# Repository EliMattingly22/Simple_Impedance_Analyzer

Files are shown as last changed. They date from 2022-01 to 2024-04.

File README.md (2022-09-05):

# Simple Impedance Analyzer

## Purpose

The impedance analyzer was designed as a low-cost, flexible, and accurate platform to perform impedance measurement at arbitrary frequencies up to ~250kHz. The current infrastructure assumes the user has access to a National Instruments DAQ (e.g. NI-USB-6363), though similar digitizers would be similarly effective. 

In this current configuration:
* About 0.1% Accuracy for large impedance and frequency ranges.
* The LabView has an easy to use GUI
* TDMS file saving
* It can measure impedances from 10mOhms to 10MOhms, and by changing the shunt resistor values that range could be extended 
* Test at frequencies from DC-250kHz (>100kHz still needs validation)
* Perform frequency sweeps on log or linear spacing
* If a battery-powered computer and DAQ is used, the entire measurement apparatus can be both portable and floating.



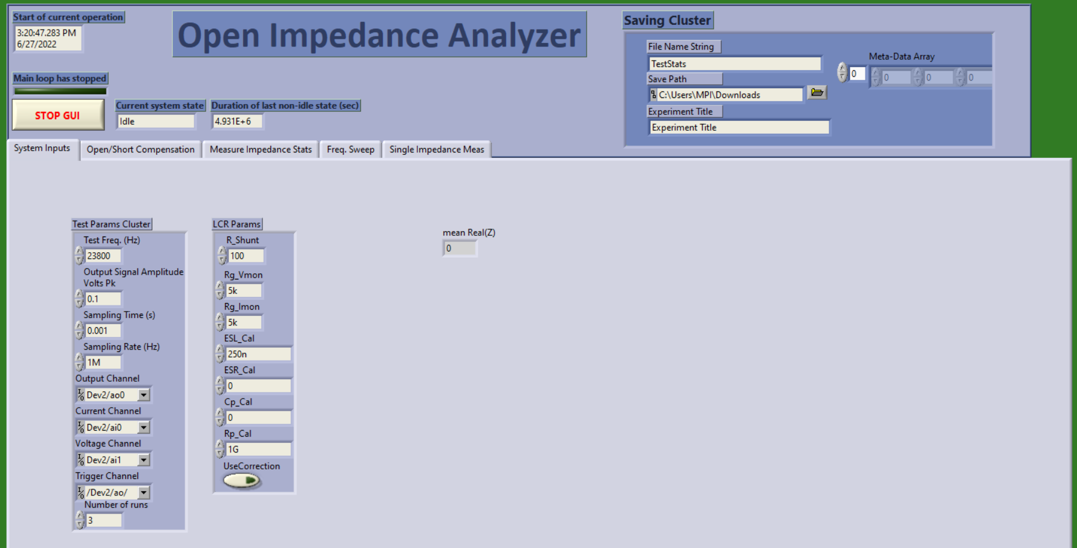
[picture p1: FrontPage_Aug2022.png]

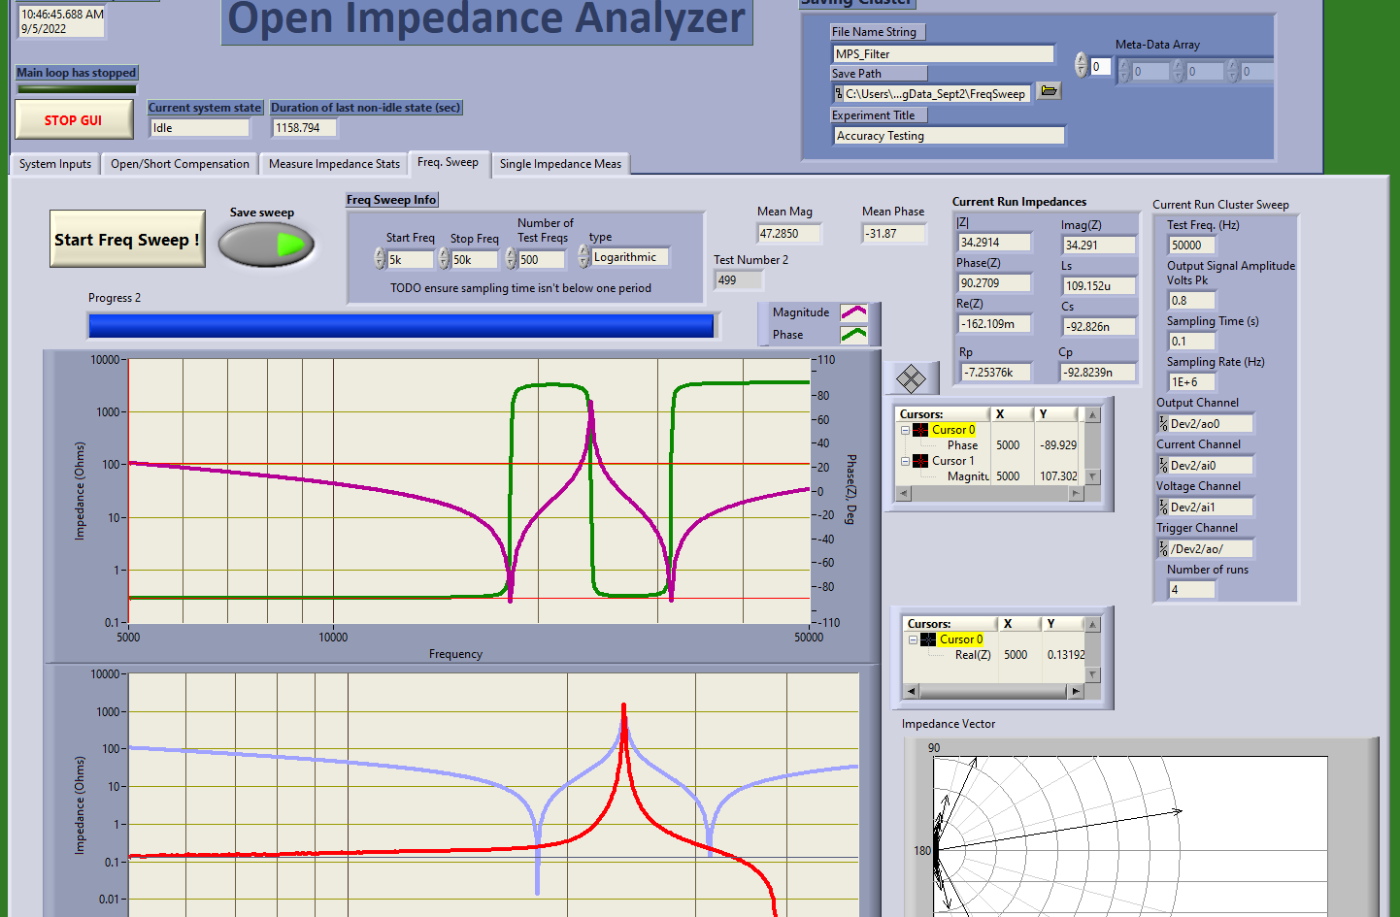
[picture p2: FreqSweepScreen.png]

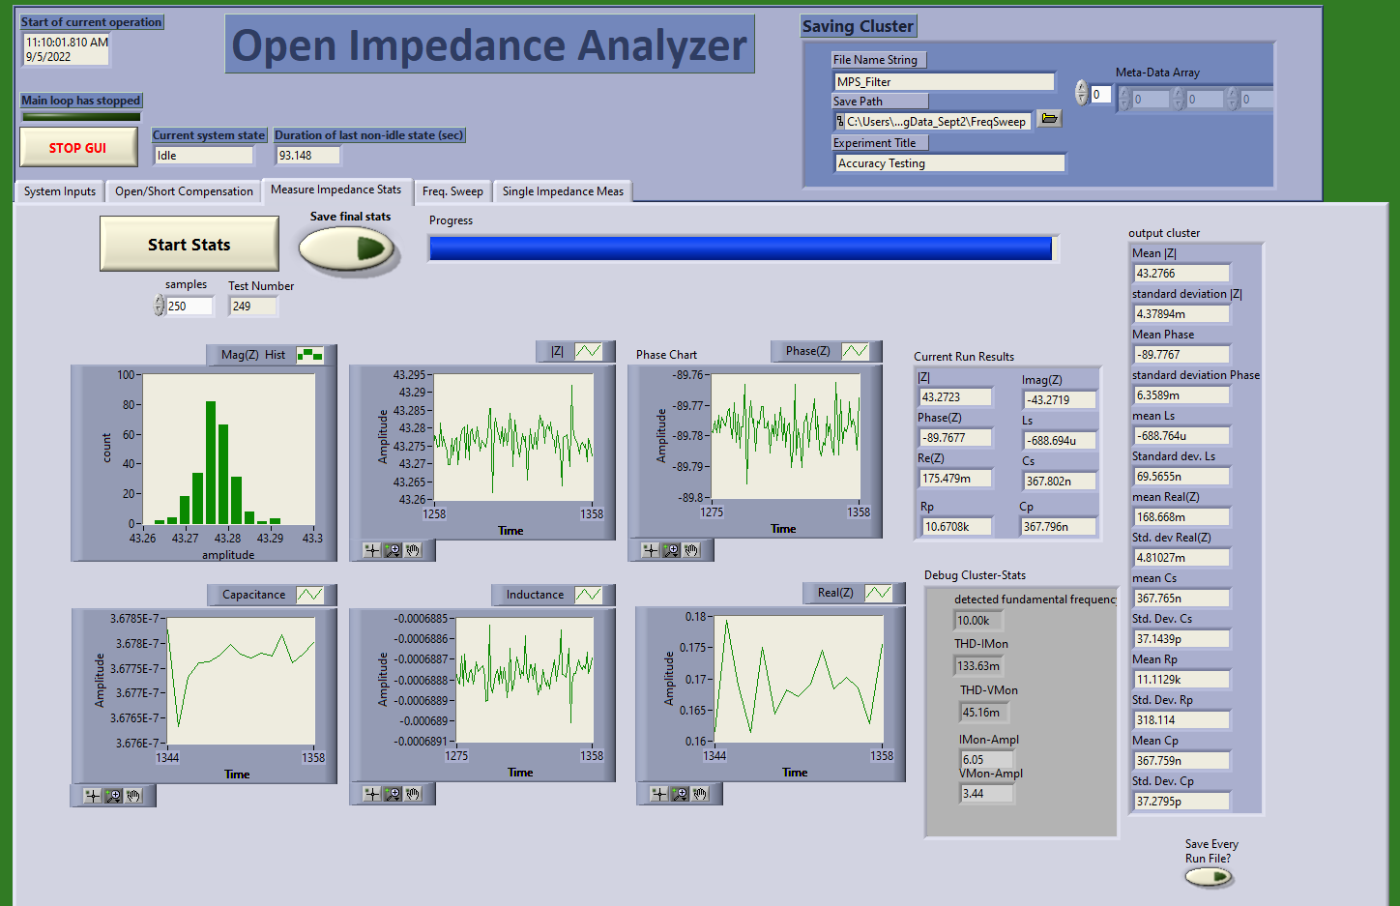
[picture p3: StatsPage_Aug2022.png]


### Accuracy and noise (1 kHz resistive)
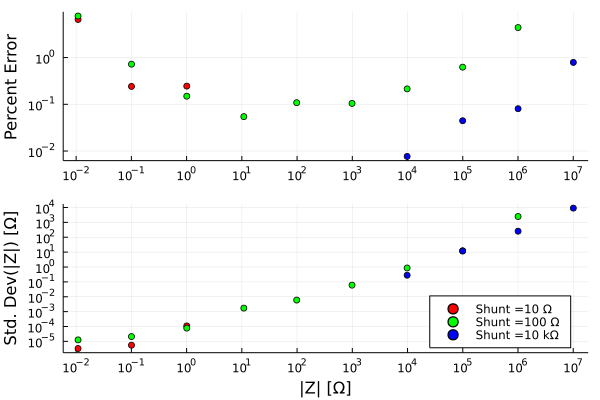
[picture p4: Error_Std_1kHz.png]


### Accuracy and noise (10 kHz resistive)
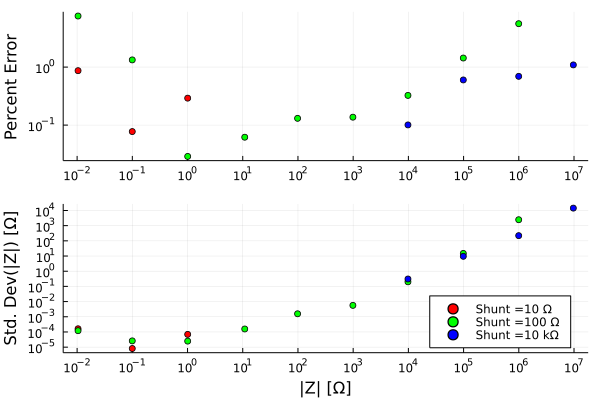
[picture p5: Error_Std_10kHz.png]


### Accuracy and noise (100 kHz resistive)
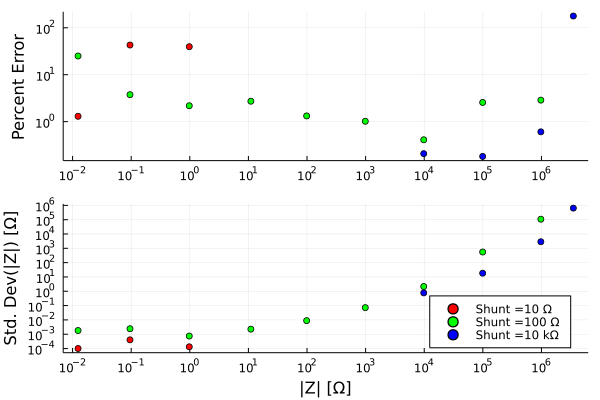
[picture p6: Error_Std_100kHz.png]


### Accuracy and noise (10 kHz Capacitors)
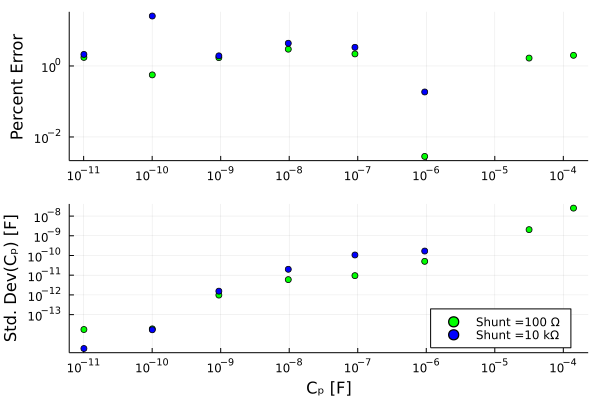
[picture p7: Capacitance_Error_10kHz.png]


* It seems one can expect about 1% accuracy between 10 p to 0.1 mF. 
* The point indicating 0.01% accuracy is probably spurious. Some random errors happened to offset each others. 

# PCB
Use V2 rev B. V3 has not been tested/built. it is still in design phase. Perhaps it should just be in a separate brach of Github. Designed in KiCAD v6.

# Operating Principle
This circuit uses the "auto-balancing bridge" technique. If you are curious/want to play around with the circuit you can see the LTSPICE schematic. 

It is worth reading the [Keysight impedance measurement handbook](https://www.keysight.com/us/en/assets/7018-06840/application-notes/5950-3000.pdf) or TI's reference design for an LCR meter front-end for an overview of measurement techniques. 

The current through the DUT is (ideally) the same as the current in the shunt resistor, so the impedance is V(DUT) / (V(Shunt)/R(Shunt)). 

# Source of Errors

The precision of the circuit is dominated by the shunt resistors and gain accuracy of the INAs. Error in any of these will linearly cause an error in the calculated impedance. If they are stable over time, they can conceivably be calibrated with a high tolerance (e.g. 0.01%) reference resistor.

If the shunt resistor is off by some value, *X* (where 1.01 would be 1% higher than nominal), the current would be reported as I<sub>0</sub>**X* where I<sub>0</sub> is the actual current. 

The noise performance of the INAs isn't great, but the FET inputs have extremely low bias currents, and low current noise, which are necessary if high impedance loads are attached. The noise should add an incoherent error, so by averaging for longer, this can be mitigated. 

The parasitic elements can be accounted for by taking an open/short/load measurement. See sect. 4.3.2 in the impedance measurement handbook

# Operation instructions
## Setup
The device should be plugged in with a four-wire (Kelvin) probe attached. On the probe there will be two pairs of leads, each connected to a clamp (typically one pair is red, one is black). The two BNC connections on the red lead should be plugged into the "HPot" and "HCur" connectors, and the BNCs on the black probe should be connected to "LPot" and "HPot" connectors. 

Plug in the power and make sure the LEDs next to the "+5V" and "-5V" are illuminated. 

The DAQ should be plugged in via the BNC connectors and however they are connected, those outputs/inputs are selected on the front page of the Labview GUI.

Also on the front page, set the sampling rate to the maximum allowable (see documentation for your DAQ). Set the sampling time to be >10 periods of whatever frequency you are testing at. Longer gives better noise performance.

For the shunt resistor, use the value most similar to the load you are measuring. Use J13/14 to select the shunt resistor. 

Set the series resistor before the load (R9/24) to the same value as the shunt resistor using J17.
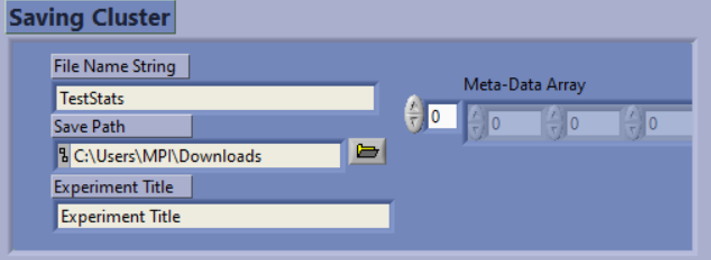
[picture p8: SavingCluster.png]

* For the saving cluster the Fine Name String will be the identifier in the file name.
* Save path is the directory it will be saved within
* Experiment title is a string added to the metadata
* Meta-data array is an array that the user can fill in as desired. It just goes into meta-data as-is. For example, if you are measuring the turns on an inductor vs inductance, you could enter the turn count in this spot and then afterwards when processing the data it would already be saved. 

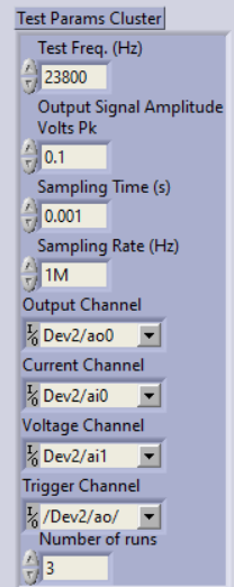
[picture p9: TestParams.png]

* **Test Freq:** This is the measurement frequency for single measurements and stats. It is overwritten for frequency sweeps.
* **Output Signal Amp:** This is the waveform amplitude the DAQ outputs. If this is too low, SNR is sacrificed, if it is too high, the waveform can clip. Check the debugging cluster to ensure the amplitude of the voltage monitor and current monitor arent clipping (i.e. they are less than 7 V or so)
* **Sampling time:** Time of acquisition in seconds. Should be long enough for 10 or so periods of the output waveform. More improves SNR. 
* **Sampling Rate:** Sampling rate in Hz. should be maximum allowable.
* **Output Channel:** The channel that goes into the Voltage Input BNC (top left in photo above)
* **Current Channel:** The channel that comes from the current sense BNC (Bottom left in photo above)
* **Voltage channel:** The channel that comes from the voltage sense BNC (middle left in photo above)
* **Trigger channel:** This should be set to the output start trigger, for example "/Dev2/ao/StartTrigger"
* **Number of runs:** this is the number of times the acquisition will be repeated and averaged.

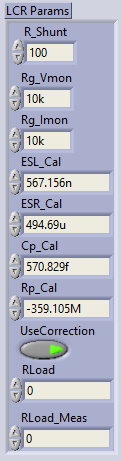
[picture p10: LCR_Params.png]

* **R_Shunt:** The shunt resistor value (R14/18)
* **Rg_Vmon:** The gain-setting resistor for the voltage monitor (R12 or R8) 
* **Rg_Imon:** The gain-setting resistor for the current monitor (R11 or R7) 
* **ESL_Cal:** This value is set by the short circuit compensation and is enabled by the UseCorrection boolean
* **ESR_Cal:** This value is set by the short circuit compensation and is enabled by the UseCorrection boolean
* **Cp_Cal:** This value is set by the open circuit compensation and is enabled by the UseCorrection boolean
* **Rp_Cal:** This value is set by the open circuit compensation and is enabled by the UseCorrection boolean

* **UseCorrection:** enables the short/open compensation values. Typically set to TRUE (green illuminated)

* **RLoad:** This is the actual value of the load compensation resistor that one may use to calibrate gain errors of the system. 

* **RLoad_Meas:** This is the measured value of that load. To acquire this value, set RLoad and RLoad_Meas to 0 and then measure the known load and set this and the RLoad by typing in the appropriate values.

## Calibration
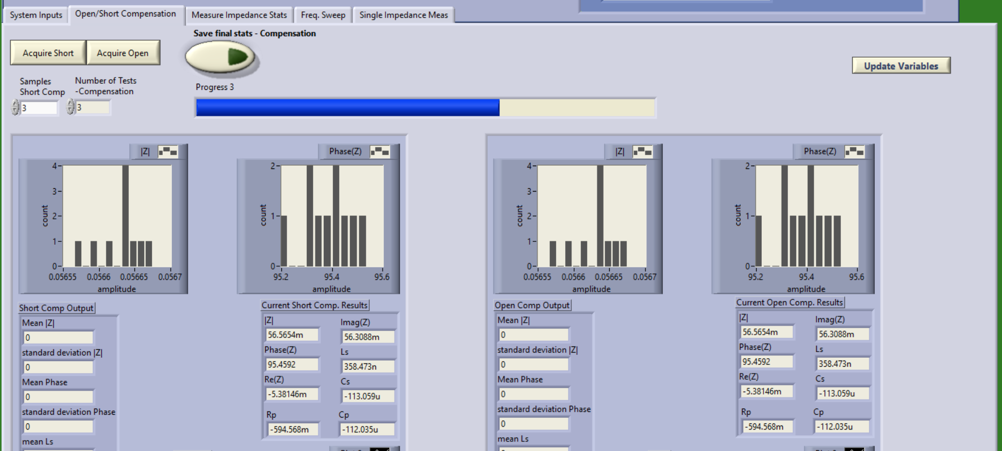
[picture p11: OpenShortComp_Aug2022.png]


Set the equipment up to measure your load, and short the clips together. Next, go to the Short/Open compensation tab and press the "Acquire short" button. Open the clips and then do the open compensation.

## Measure load

Use the last page to do a single impedance measurement and ensure the load is similar to expected. Then use the stats page or freq sweep depending on what you want. 

## List of jumpers & their purpose
* J15/16 low-pass filters for the input. These clean the analog signal from the DAQ. They can generally be set to the highest frequency that the user plans to measure. Removing the jumper disconnects the filtering entirely.

* J10: The current monitor gain selection
* J12: Voltage monitor gain selection
* J13/14: Shunt resistor selection
* J17: Series resistor selection. This resistor in series with the load helps stability and makes the system more balanced. The resistor value should match the shunt resistor value.

# If you are having errors:
1) Make sure the channels are selected properly
2) Make sure BOTH sides of the clips are on the load
3) Make sure the BNCs are properly attached
4) The LEDs should be illuminated
5) The amplitude should be sufficiently low that it doesn't saturate the inputs/clip

# Example applications:

## Litz wire, air-core inductor
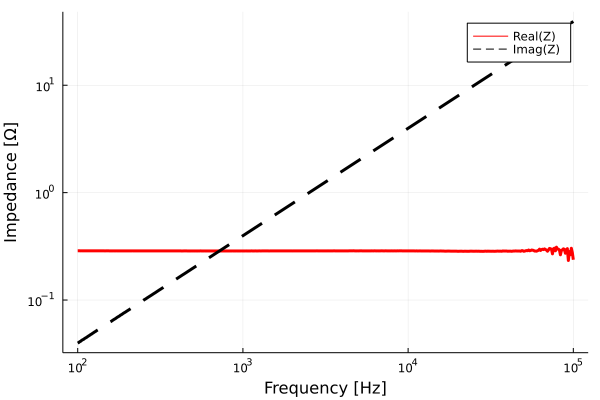
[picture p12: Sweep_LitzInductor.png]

* The impedance is exactly as expected here for an inductor. Because Litz wire was used, the resistance is not a strong function of frequency. 
* The slope of the reactance is constant and proportional to frequency.

## Skin and proximity effect on inductor
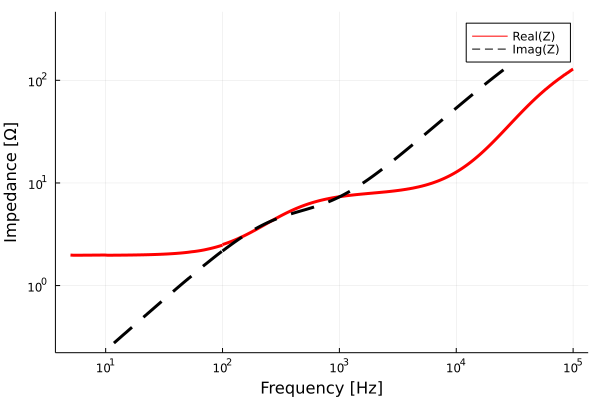
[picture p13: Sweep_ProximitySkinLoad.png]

This is a frequency sweep of a solenoid (~1 mm diameter) wound on a copper tube with a wall-thickness of ~1 mm. Quite a lot is happening with this load:
* Below 50 Hz or so, it is essentially a resistor, the inductive impedance is very small. 
* At 50-1k Hz, the solenoid's impedance has an increasing real component and decreasing inductance (decreasing slope of imag.). This occurs as the inductor couples more strongly into the copper tube. The inductance decreases because the magnetic field in the center of the tube is decreasing as the wall effectively shields it. 
* Between 1k and 10k Hz the resistance nearly plateaus and the inductance starts rising proportionally to frequency. Presumably at this point, the skin depth of the copper tube has been met, so the magnetic fields are not significantly penetrating to the center of the tube. 
* Above 10 kHz the skin depth of the wire is being reached and the AC-resistance is increasing as the effective copper area for current to flow in decreases.

## Resonant L-C
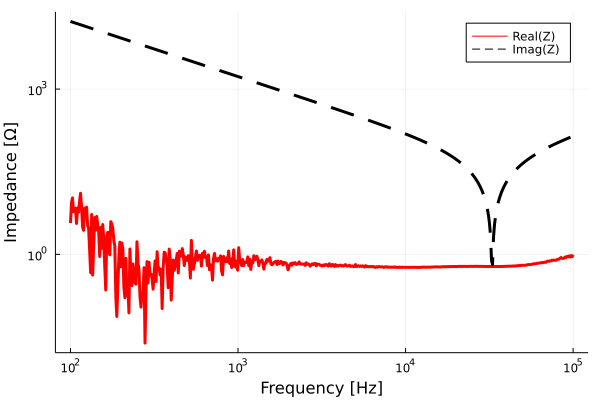
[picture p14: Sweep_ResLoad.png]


## Notch filter input
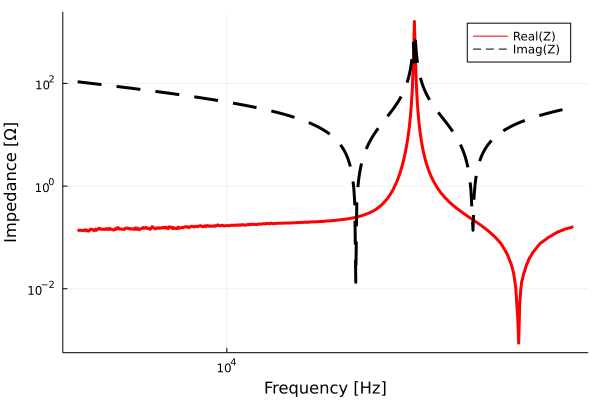
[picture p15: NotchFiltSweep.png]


# Thoughts for improvement
* Make the shunt resistor digitally selectable
* Build a microcontroller-based interface for increased portability
* Improve system accuracy for high impedance loads
* Improve system accuracy for high frequencies
* Modify it such that it uses only one amplifier for both VMon and IMon and a relay to select which one. 
* Replace INA121 with a JFET INA (e.g. 3 opamp configuration)
* Implement transformer test jig

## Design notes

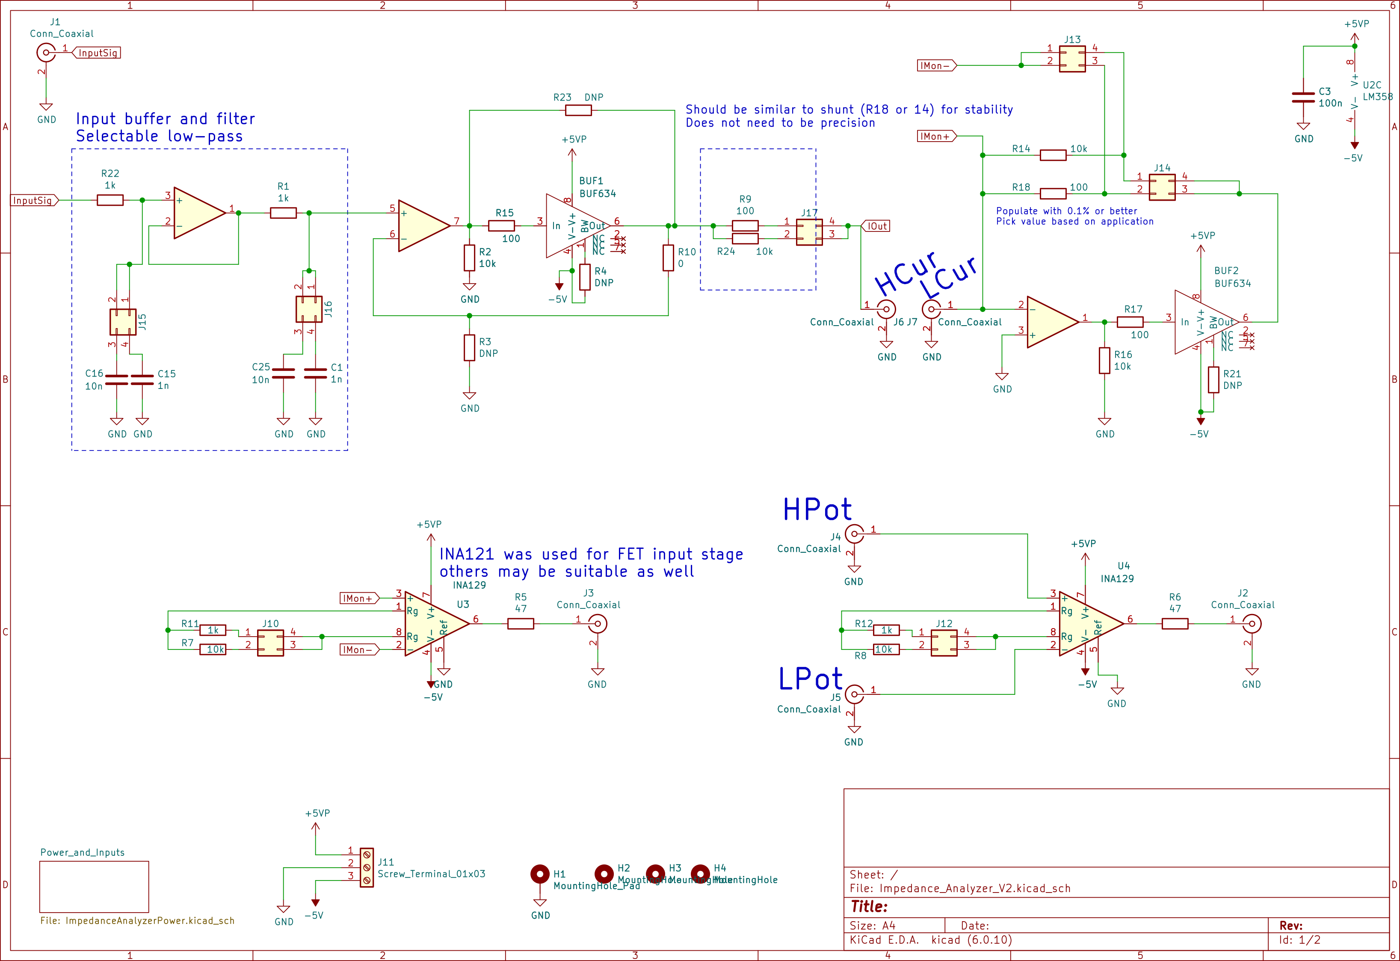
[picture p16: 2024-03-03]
Impedance_Analyzer_V2_KiCAD/Schematic.png

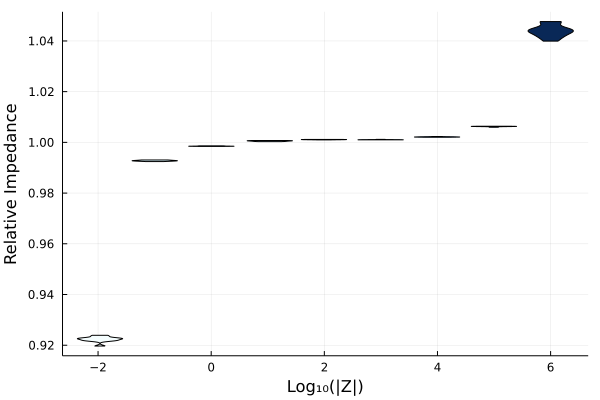
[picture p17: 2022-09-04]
RelativeImpedance_1kHz.png

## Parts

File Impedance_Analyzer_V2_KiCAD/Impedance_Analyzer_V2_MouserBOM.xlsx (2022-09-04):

Comment | Designator | Footprint | Mouser PN
BUF634 | BUF1,BUF2 | Package_SO:SO-8_3.9x4.9mm_P1.27mm | 595-BUF634AIDR
1n | C1,C15 | Capacitor_SMD:C_0805_2012Metric
10n | C16,C25 | Capacitor_SMD:C_0805_2012Metric
C_Polarized | C2,C11,C12,C13 | Capacitor_SMD:C_1206_3216Metric_Pad1.33x1.80mm_HandSolder | 603-CC126KKX7R8BB106
100n | C3,C5,C8,C10,C14,C17,C18,C19,C20,C21,C22,C23,C24 | Capacitor_SMD:C_0805_2012Metric
22u | C4,C6 | Capacitor_THT:CP_Radial_D5.0mm_P2.00mm | 710-860010372006 (https://www.mouser.com/ProductDetail/710-860010372006)
CP | C7,C9 | Capacitor_THT:CP_Radial_D8.0mm_P5.00mm | 667-ECA-1CM331B (https://www.mouser.com/ProductDetail/667-ECA-1CM331B)
D | D1 | Diode_SMD:D_SMA
D_TVS | D2,D6 | Diode_SMD:D_SMA | 621-SMAJ18CA-13-F (https://www.mouser.com/ProductDetail/621-SMAJ18CA-13-F)
LED | D3,D4,D5 | LED_SMD:LED_1206_3216Metric
Ferrite_Bead | FB1 | Resistor_SMD:R_0805_2012Metric
MountingHole_Pad | H1 | MountingHole:MountingHole_4.3mm_M4_Pad
MountingHole | H2,H3,H4 | MountingHole:MountingHole_4mm
Conn_Coaxial | J1,J2,J3,J4,J5,J6,J7 | Connector_Coaxial:BNC_TEConnectivity_1478204_Vertical | 571-413631-1
Conn_02x02_Counter_Clockwise | J10,J12,J13,J14,J15,J16,J17 | Connector_PinHeader_2.54mm:PinHeader_2x02_P2.54mm_Vertical | 855-M20-9980245
Screw_Terminal_01x03 | J11 | TerminalBlock:TerminalBlock_bornier-3_P5.08mm
Barrel_Jack_Switch | J8 | Connector_BarrelJack:BarrelJack_Horizontal
USB_B_Micro | J9 | Connector_USB:USB_Micro-B_Wuerth_629105150521 | 710-629105150521 (https://www.mouser.com/ProductDetail/710-629105150521)
10u | L1,L2 | Inductor_SMD:L_Taiyo-Yuden_NR-60xx_HandSoldering | 963-NR6045T100M (https://www.mouser.com/ProductDetail/963-NR6045T100M)
1k | R1,R11,R12,R13,R19,R20,R22 | Resistor_SMD:R_1206_3216Metric
0 | R10 | Resistor_SMD:R_1206_3216Metric
50 | R15,R17 | Resistor_SMD:R_1206_3216Metric
10k | R2,R7,R8,R14,R16,R24 | Resistor_SMD:R_1206_3216Metric | 284-APC1206B10K0N
DNP | R3,R4,R21,R23 | Resistor_SMD:R_1206_3216Metric
47 | R5,R6 | Resistor_SMD:R_1206_3216Metric
100 | R9,R18 | Resistor_SMD:R_1206_3216Metric | 71-TNPW1206100RBYEN
DPUN02L-XX | Reg1 | Martinos:SIP-2W-7 | 709-DPUN02L-05 (https://www.mouser.com/ProductDetail/709-DPUN02L-05)
OPA2830 | U1,U2 | Package_SO:SO-8_3.9x4.9mm_P1.27mm | 595-OPA2830IDR (https://www.mouser.com/ProductDetail/595-OPA2830IDR)
INA121 | U3,U4 | Package_DIP:DIP-8_W7.62mm | 595-INA121PA (https://www.mouser.com/ProductDetail/595-INA121PA)
L7805 | U5 | Package_TO_SOT_THT:TO-220-3_Vertical
Shorting pins | Order 10+ |  | 571-28815452

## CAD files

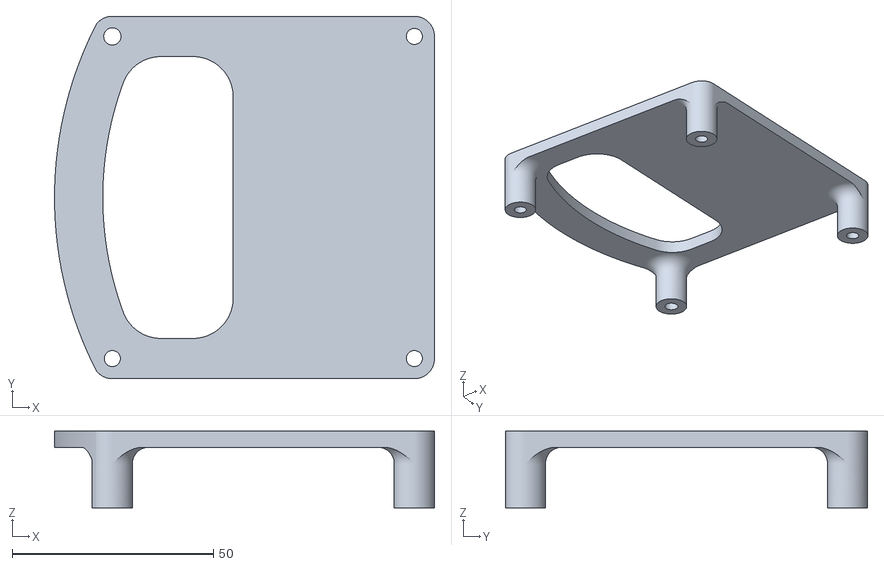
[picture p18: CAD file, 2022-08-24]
3D print case/TopCase.stl
94.4 x 90.0 x 19.0

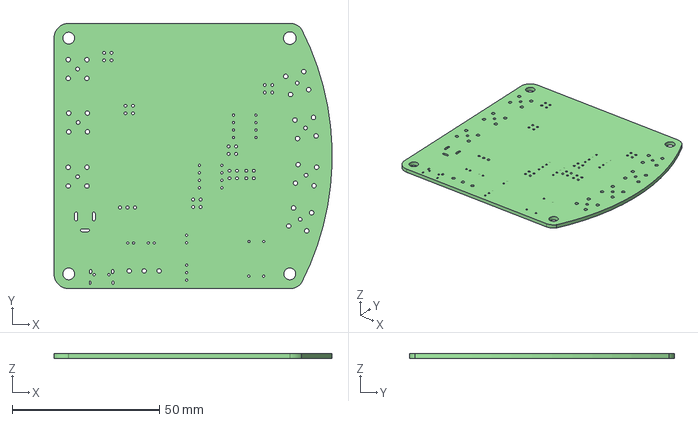
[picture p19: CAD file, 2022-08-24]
Impedance_Analyzer_V2_KiCAD/Impedance_Analyzer_V2.step
94.3 x 90.0 x 1.60 mm

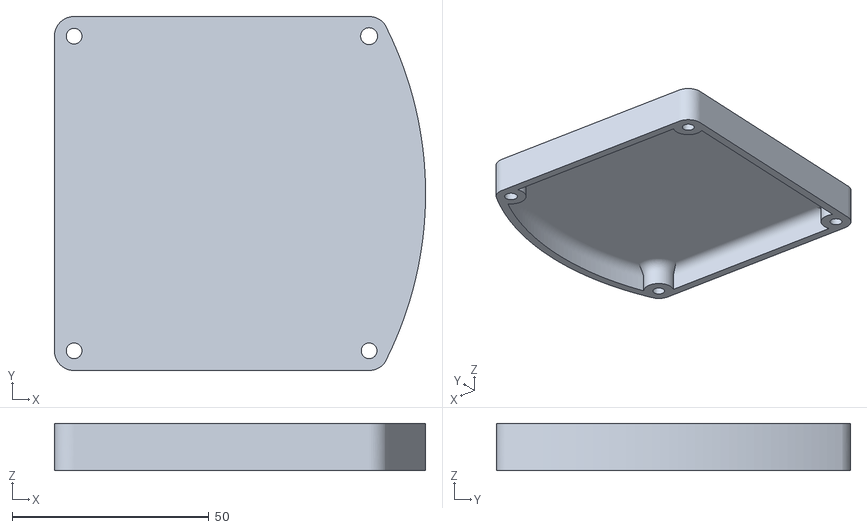
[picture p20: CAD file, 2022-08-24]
3D print case/Bottom Case.stl
94.4 x 90.0 x 12.0

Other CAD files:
3D print case/Bottom Case.ipt
3D print case/OldVersions/Bottom Case.0001.ipt
3D print case/OldVersions/TopCase.0001.ipt
3D print case/TopCase.ipt
Impedance_Analyzer_V2_KiCAD/Impedance_Analyzer_V2 PCB.ipt
Impedance_Analyzer_V2_KiCAD/Impedance_Analyzer_V2.iam
Impedance_Analyzer_V2_KiCAD/OldVersions/Impedance_Analyzer_V2.0001.iam

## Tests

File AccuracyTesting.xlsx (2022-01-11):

Component Name | Value | ET4510 (Mag) | ET4510 (Phase) | My Ztester (Mag) | My Ztester (Phase) | Agilent 4263B (Mag) | Agilent 4263B (Phase) | Mag Error Pct ET4510 | Mag Error Pct 4263B | Error Between ET4510 and 4263B | AliExpress Component tester Mag | Phase | MLC500
R1 | 0.01 | 0.0103 | 10 | 0.0107 | -30 | 0.00983 | 2 | -3.883495146 | -8.850457782 | -4.78128179
R2 | 0.1 | 0.1002 | -1 | 0.0991 | -0.1 | 0.0996 | 0.75 | 1.097804391 | 0.5020080321 | -0.6024096386 | 0.05
R3 | 1 | 1.006 | 0.55 | 1.007 | 0.6 | 1.0075 | 0.9 | -0.09940357853 | 0.04962779156 | 0.1488833747 | 0.98
R4 |  | 1.378 | 8.28 | 1.38 | 8.3 | 1.385 | 8.28 | -0.145137881 | 0.3610108303 | 0.5054151625
R5 |  | 265 | 0.01 | 264.9 | 0.045 | 264.8 | 0 | 0.03773584906 | -0.03776435045 | -0.07552870091 | 263.6
R6 |  | 9838 | 0 | 9833 | 1.6 | 9838 | 0 | 0.05082333808 | 0.05082333808 | 0
R7 |  | 99800 | 0.05 | 95800 | 15 | 99800 | 0 | 4.008016032 | 4.008016032 | 0 | 99500
L1 |  | 0.6123 | 40.96 | 0.614 | 41.5 | 0.6172 | 41.09 | -0.2776416789 | 0.518470512 | 0.7939079715 | 0.66 | 0
L2 |  | 18.15 | 77.69 | 18.2 | 78 | 18.17 | 77.6 | -0.2754820937 | -0.1651073198 | 0.1100715465 | 16.25976968 | 75.03041576 | 284.2u
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

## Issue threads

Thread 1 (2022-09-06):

### ISSUE TITLE
Request: PDF of schematics

### ISSUE THREAD

**Issue by Fliptron** [EliMattingly22/Simple_Impedance_Analyzer#1]
Hi Eli,
Kicad is not used by everybody. Please include a PDF for the schematic, that is updated whenever the schematic is updated.
Thanks

**Comment by EliMattingly22** [comment]
Good suggestion. PDF added for current revision (V2 revB) in its respective directory. Future revisions will have PDFs
[Impedance_Analyzer_V2.pdf](https://github.com/EliMattingly22/Simple_Impedance_Analyzer/blob/main/Impedance_Analyzer_V2_KiCAD/Impedance_Analyzer_V2.pdf)

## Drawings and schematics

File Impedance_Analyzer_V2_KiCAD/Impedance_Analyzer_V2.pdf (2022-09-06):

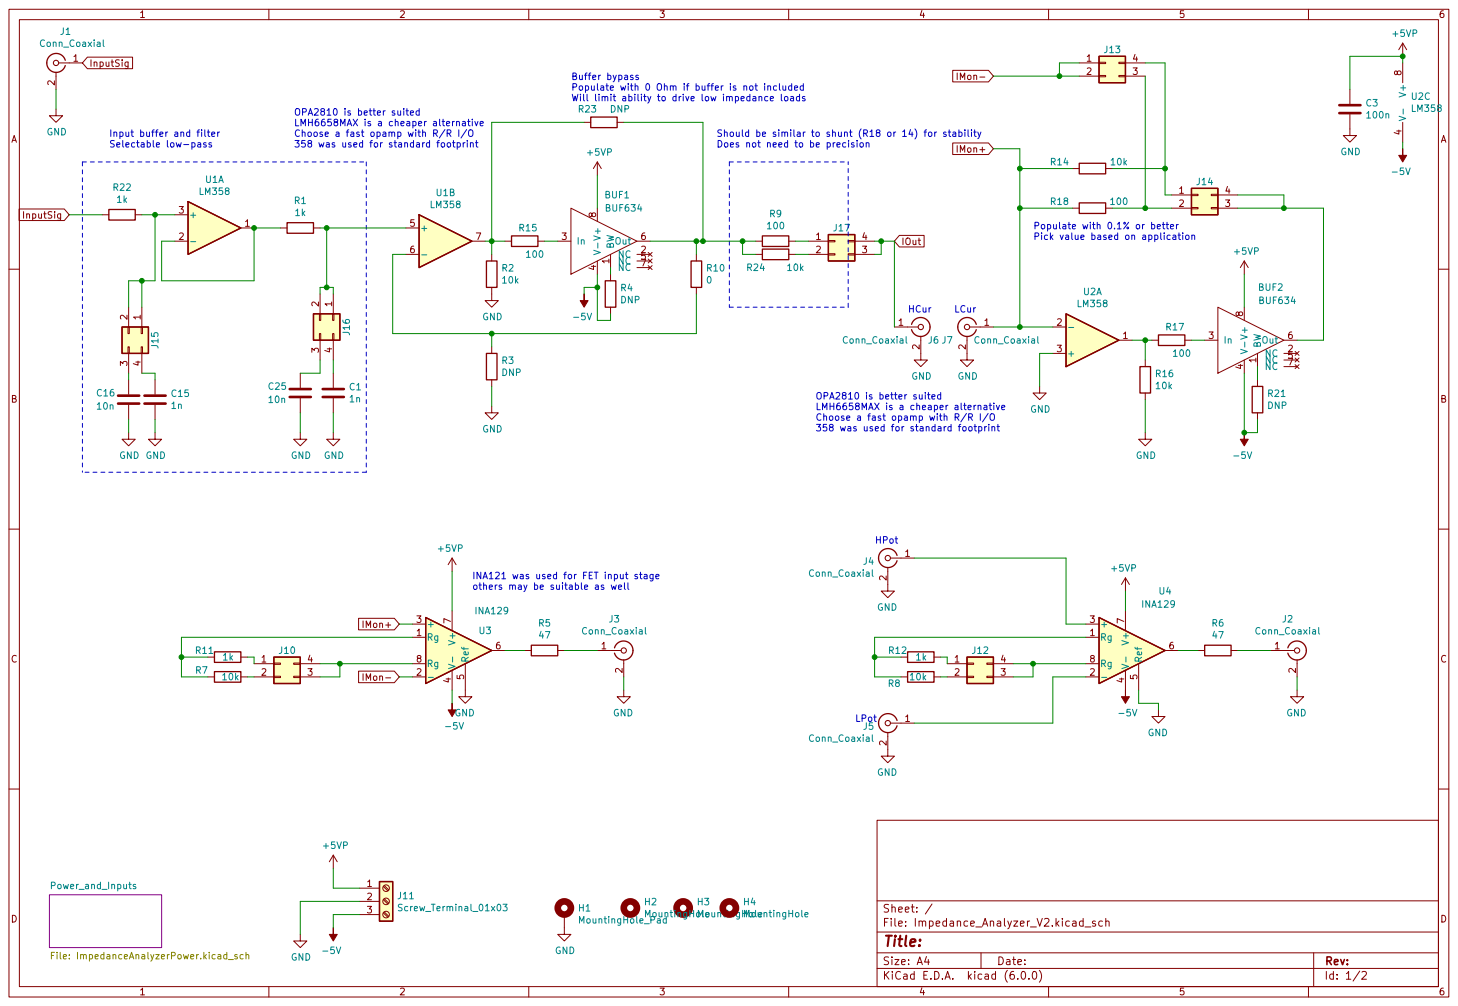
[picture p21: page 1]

Populate with 0 Ohm if buffer is not included
Will limit ability to drive low impedance loads

IMon+ OPA2810 is better suited
LMH6658MAX is a cheaper alternative
Choose a fast opamp with R/R I/O
358 was used for standard footprint

Input buffer and filter
Selectable low-pass

Should be similar to shunt (R18 or 14) for stability
Does not need to be precision

Pick value based on application OPA2810 is better suited

Populate with 0.1% or better

INA121 was used for FET input stage

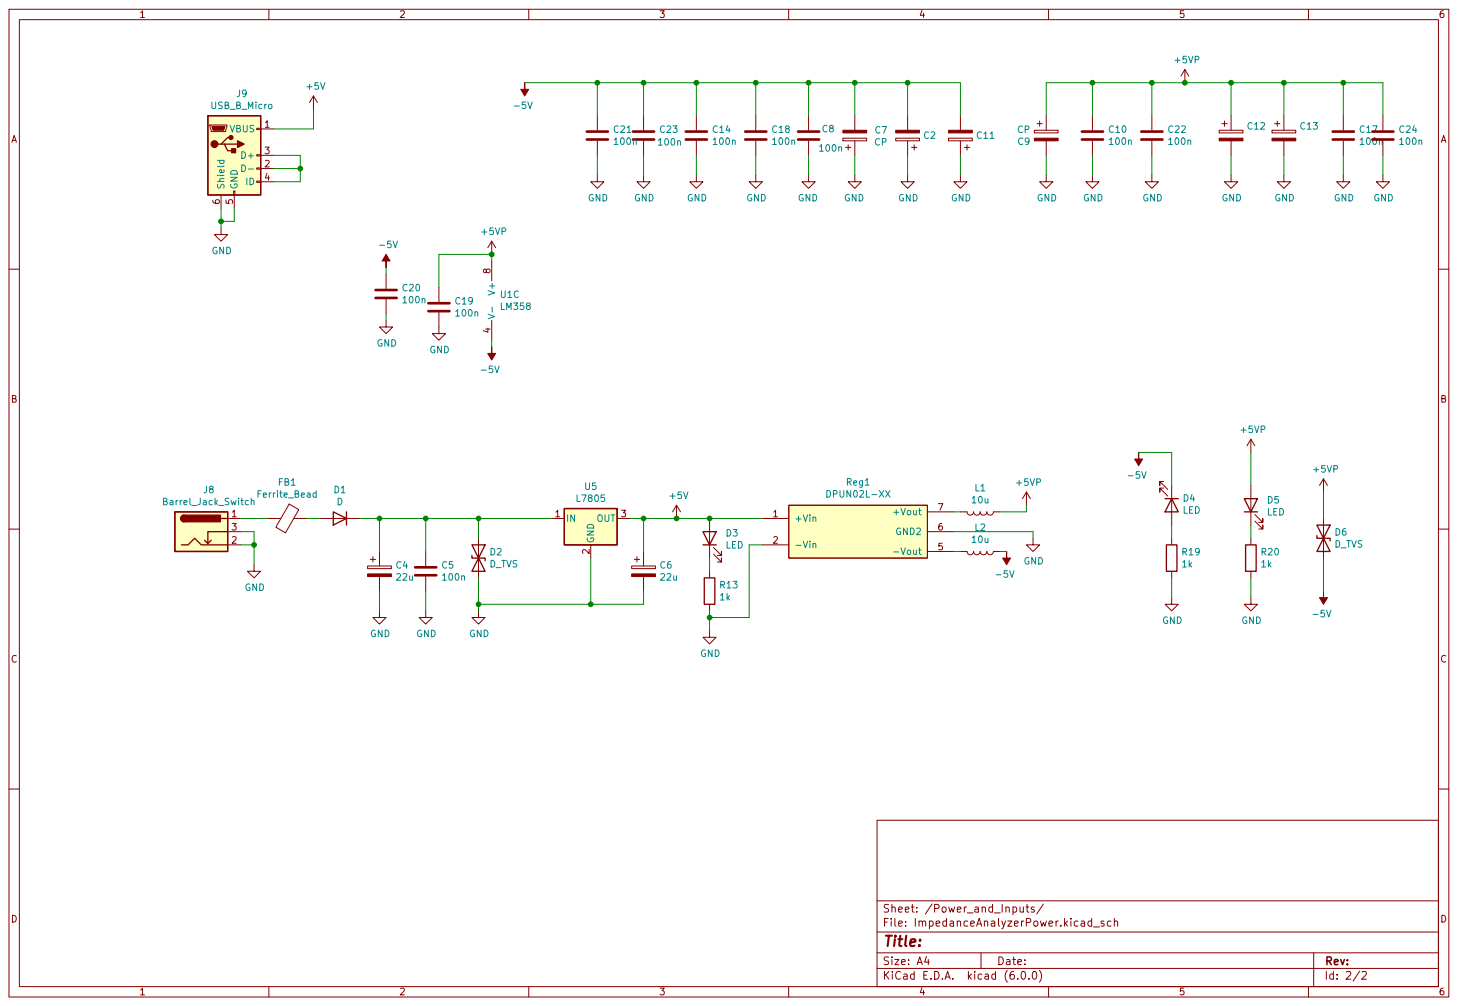
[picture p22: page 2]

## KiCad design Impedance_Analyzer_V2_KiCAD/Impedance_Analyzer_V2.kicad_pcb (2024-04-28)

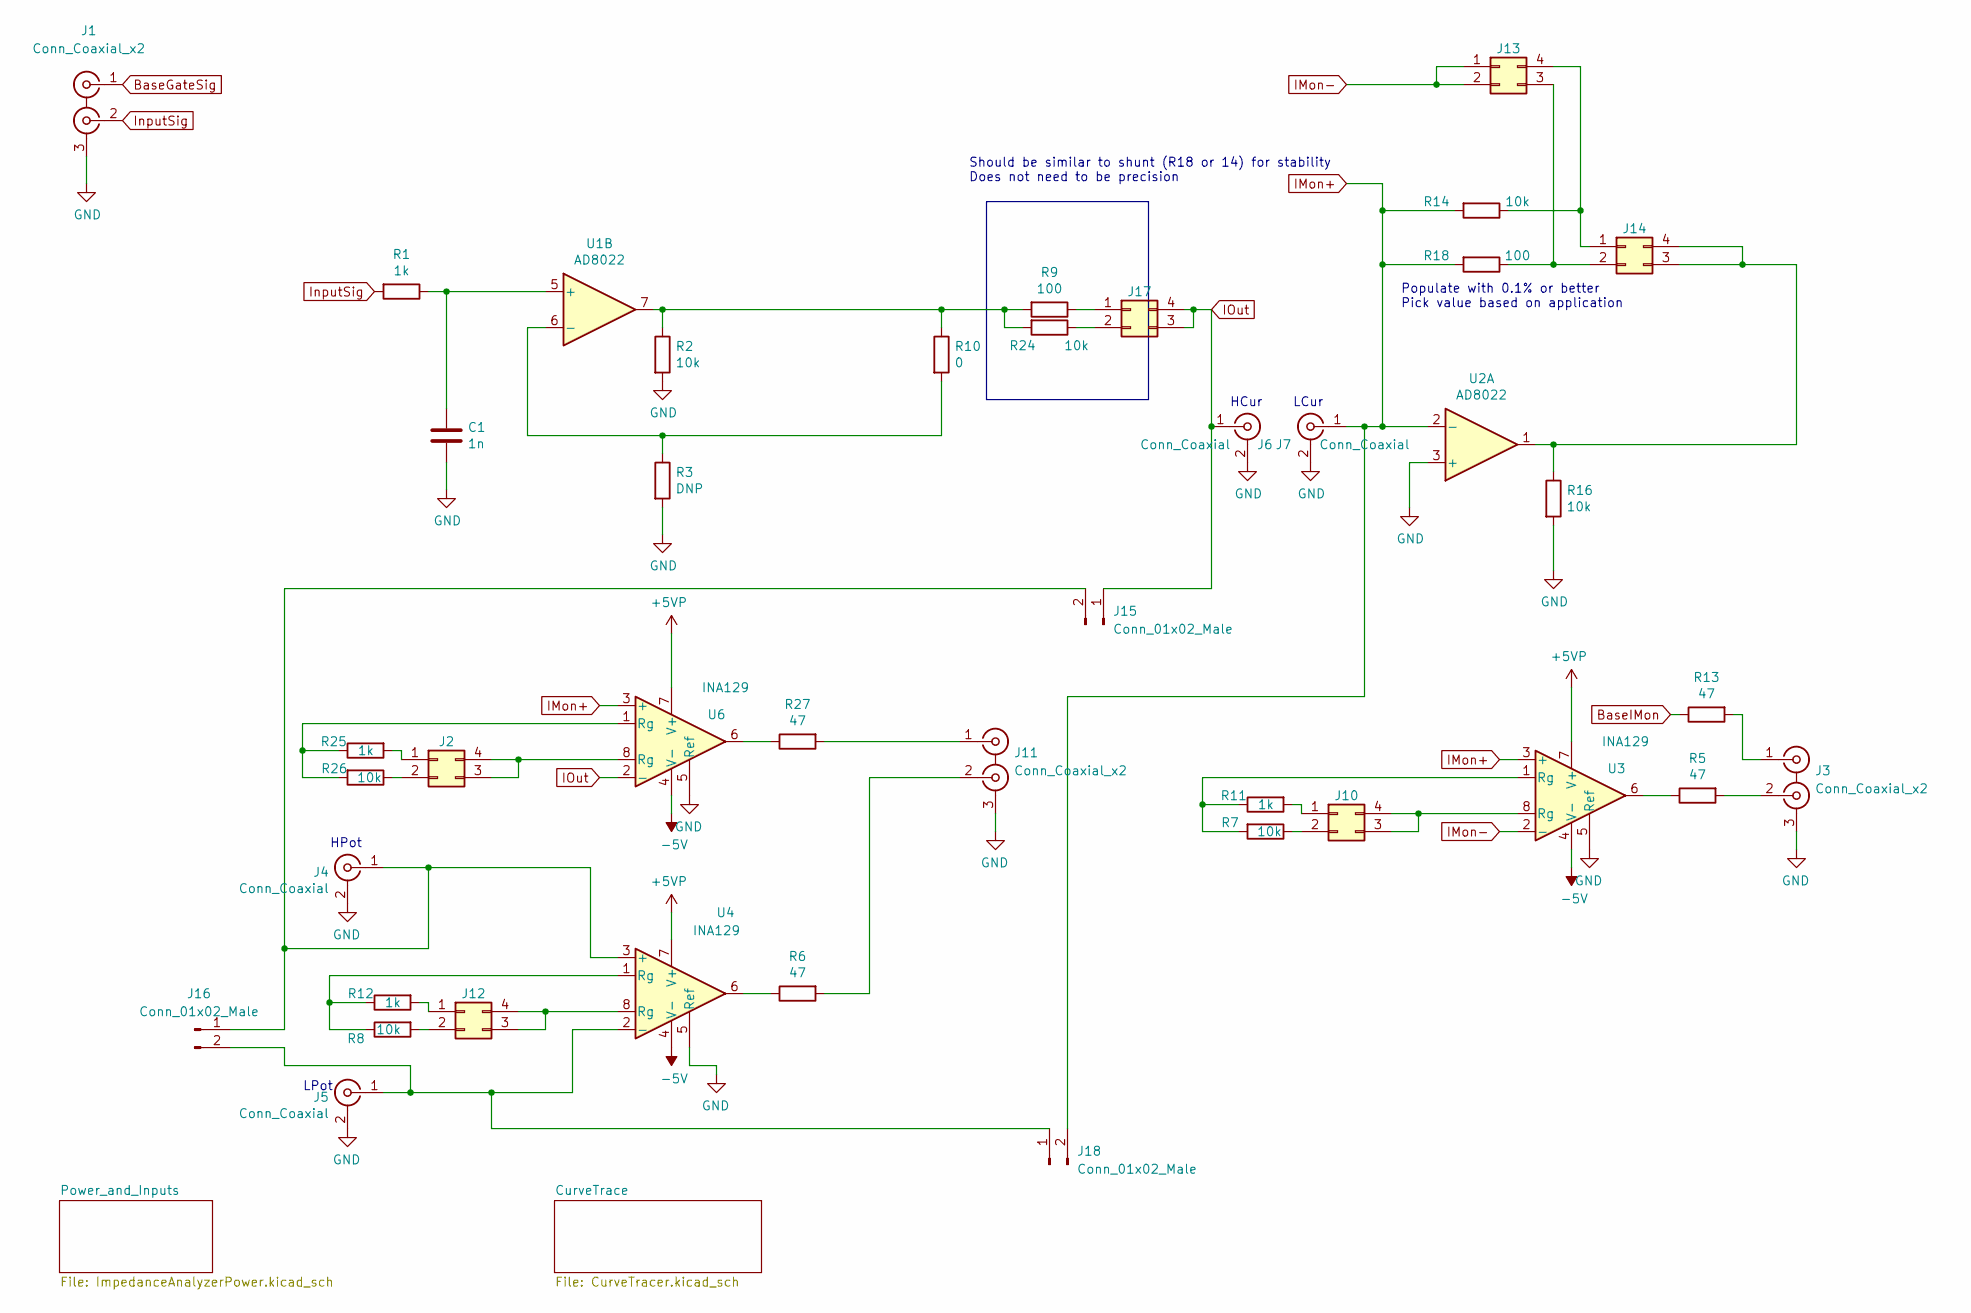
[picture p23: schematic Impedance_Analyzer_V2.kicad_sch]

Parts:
C1: 1n; C_0805_2012Metric
J1, J3, J11: Conn_Coaxial_x2; BNC_Win_364A2x95_Horizontal
J2, J10, J12, J13, J14, J17: Conn_02x02_Counter_Clockwise; PinHeader_2x02_P2.54mm_Vertical
J4, J5, J6, J7: Conn_Coaxial; 31-5486-1010 BNC Panel RA
J15, J16, J18: Conn_01x02_Male; PinHeader_1x02_P2.54mm_Horizontal
R1, R11, R12, R25: 1k; R_1206_3216Metric
R2, R7, R8, R14, R16, R24, R26: 10k; R_1206_3216Metric
R3: DNP; R_1206_3216Metric
R5, R6, R13, R27: 47; R_1206_3216Metric
R9, R18: 100; R_1206_3216Metric
R10: 0; R_1206_3216Metric
U1, U2: AD8022; SO-8_3.9x4.9mm_P1.27mm
U3, U4, U6: INA129; DIP-8_W7.62mm

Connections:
+5VP: U3.7 (V+), U4.7 (V+), U6.7 (V+); also elsewhere on the board
-5V: U3.4 (V-), U4.4 (V-), U6.4 (V-); also elsewhere on the board
BaseGateSig: J1.1 (IN1); also elsewhere on the board
BaseIMon: R13.1; also elsewhere on the board
GND: C1.2, J1.3 (EXT), J3.3 (EXT), J4.2 (Ext), J5.2 (Ext), J6.2 (Ext), J7.2 (Ext), J11.3 (EXT), R2.2, R3.2, R16.2, U2.3 (+), U3.5 (Ref), U4.5 (Ref), U6.5 (Ref); also elsewhere on the board
IMon+: J7.1 (In), J18.2, R14.2, R18.2, U2.2 (-), U3.3 (+), U6.3 (+)
IMon-: J13.1, J13.2, U3.2 (-)
IOut: J6.1 (In), J15.1, J17.3, J17.4, U6.2 (-)
InputSig: J1.2 (IN2), R1.2
unnamed: C1.1, R1.1, U1.5 (+)
unnamed: J2.1, R25.2
unnamed: J2.2, R26.1
unnamed: J2.3, J2.4, U6.8 (Rg)
unnamed: J3.1 (IN1), R13.2
unnamed: J3.2 (IN2), R5.2
unnamed: J5.1 (In), J16.2, J18.1, U4.2 (-)
unnamed: J10.1, R11.2
unnamed: J10.2, R7.1
unnamed: J10.3, J10.4, U3.8 (Rg)
unnamed: J11.1 (IN1), R27.2
unnamed: J11.2 (IN2), R6.2
unnamed: J12.1, R12.2
unnamed: J12.2, R8.2
unnamed: J12.3, J12.4, U4.8 (Rg)
unnamed: J13.3, J14.2, R18.1
unnamed: J13.4, J14.1, R14.1
unnamed: J14.3, J14.4, R16.1, U2.1
unnamed: J4.1 (In), J15.2, J16.1, U4.3 (+)
unnamed: J17.1, R9.1
unnamed: J17.2, R24.1
unnamed: R5.1, U3.6
unnamed: R6.1, U4.6
unnamed: R2.1, R9.2, R10.1, R24.2, U1.7
unnamed: R3.1, R10.2, U1.6 (-)
unnamed: R7.2, R11.1, U3.1 (Rg)
unnamed: R8.1, R12.1, U4.1 (Rg)
unnamed: R25.1, R26.2, U6.1 (Rg)
unnamed: R27.1, U6.6

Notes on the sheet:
HCur
Should be similar to shunt (R18 or 14) for stability Does not need to be precision
LCur
LPot
HPot
Populate with 0.1% or better Pick value based on application

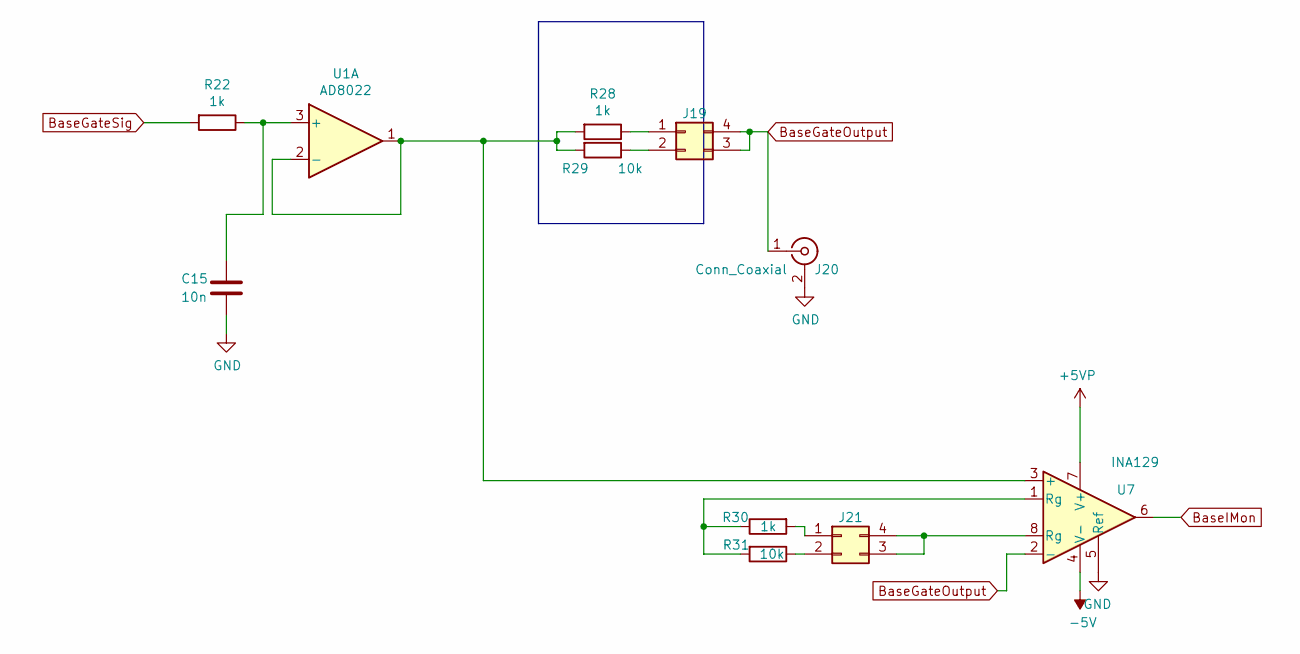
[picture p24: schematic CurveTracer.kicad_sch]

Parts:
C15: 10n; C_0805_2012Metric
J19, J21: Conn_02x02_Counter_Clockwise; PinHeader_2x02_P2.54mm_Vertical
J20: Conn_Coaxial; 31-5486-1010 BNC Panel RA
R22, R28, R30: 1k; R_1206_3216Metric
R29, R31: 10k; R_1206_3216Metric
U1: AD8022; SO-8_3.9x4.9mm_P1.27mm
U7: INA129; DIP-8_W7.62mm

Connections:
+5VP: U7.7 (V+); also elsewhere on the board
-5V: U7.4 (V-); also elsewhere on the board
BaseGateOutput: J19.3, J19.4, J20.1 (In), U7.2 (-)
BaseGateSig: R22.2; also elsewhere on the board
BaseIMon: U7.6; also elsewhere on the board
GND: C15.2, J20.2 (Ext), U7.5 (Ref); also elsewhere on the board
unnamed: C15.1, R22.1, U1.3 (+)
unnamed: J19.1, R28.1
unnamed: J19.2, R29.1
unnamed: J21.1, R30.2
unnamed: J21.2, R31.1
unnamed: J21.3, J21.4, U7.8 (Rg)
unnamed: R28.2, R29.2, U1.1, U1.2 (-), U7.3 (+)
unnamed: R30.1, R31.2, U7.1 (Rg)

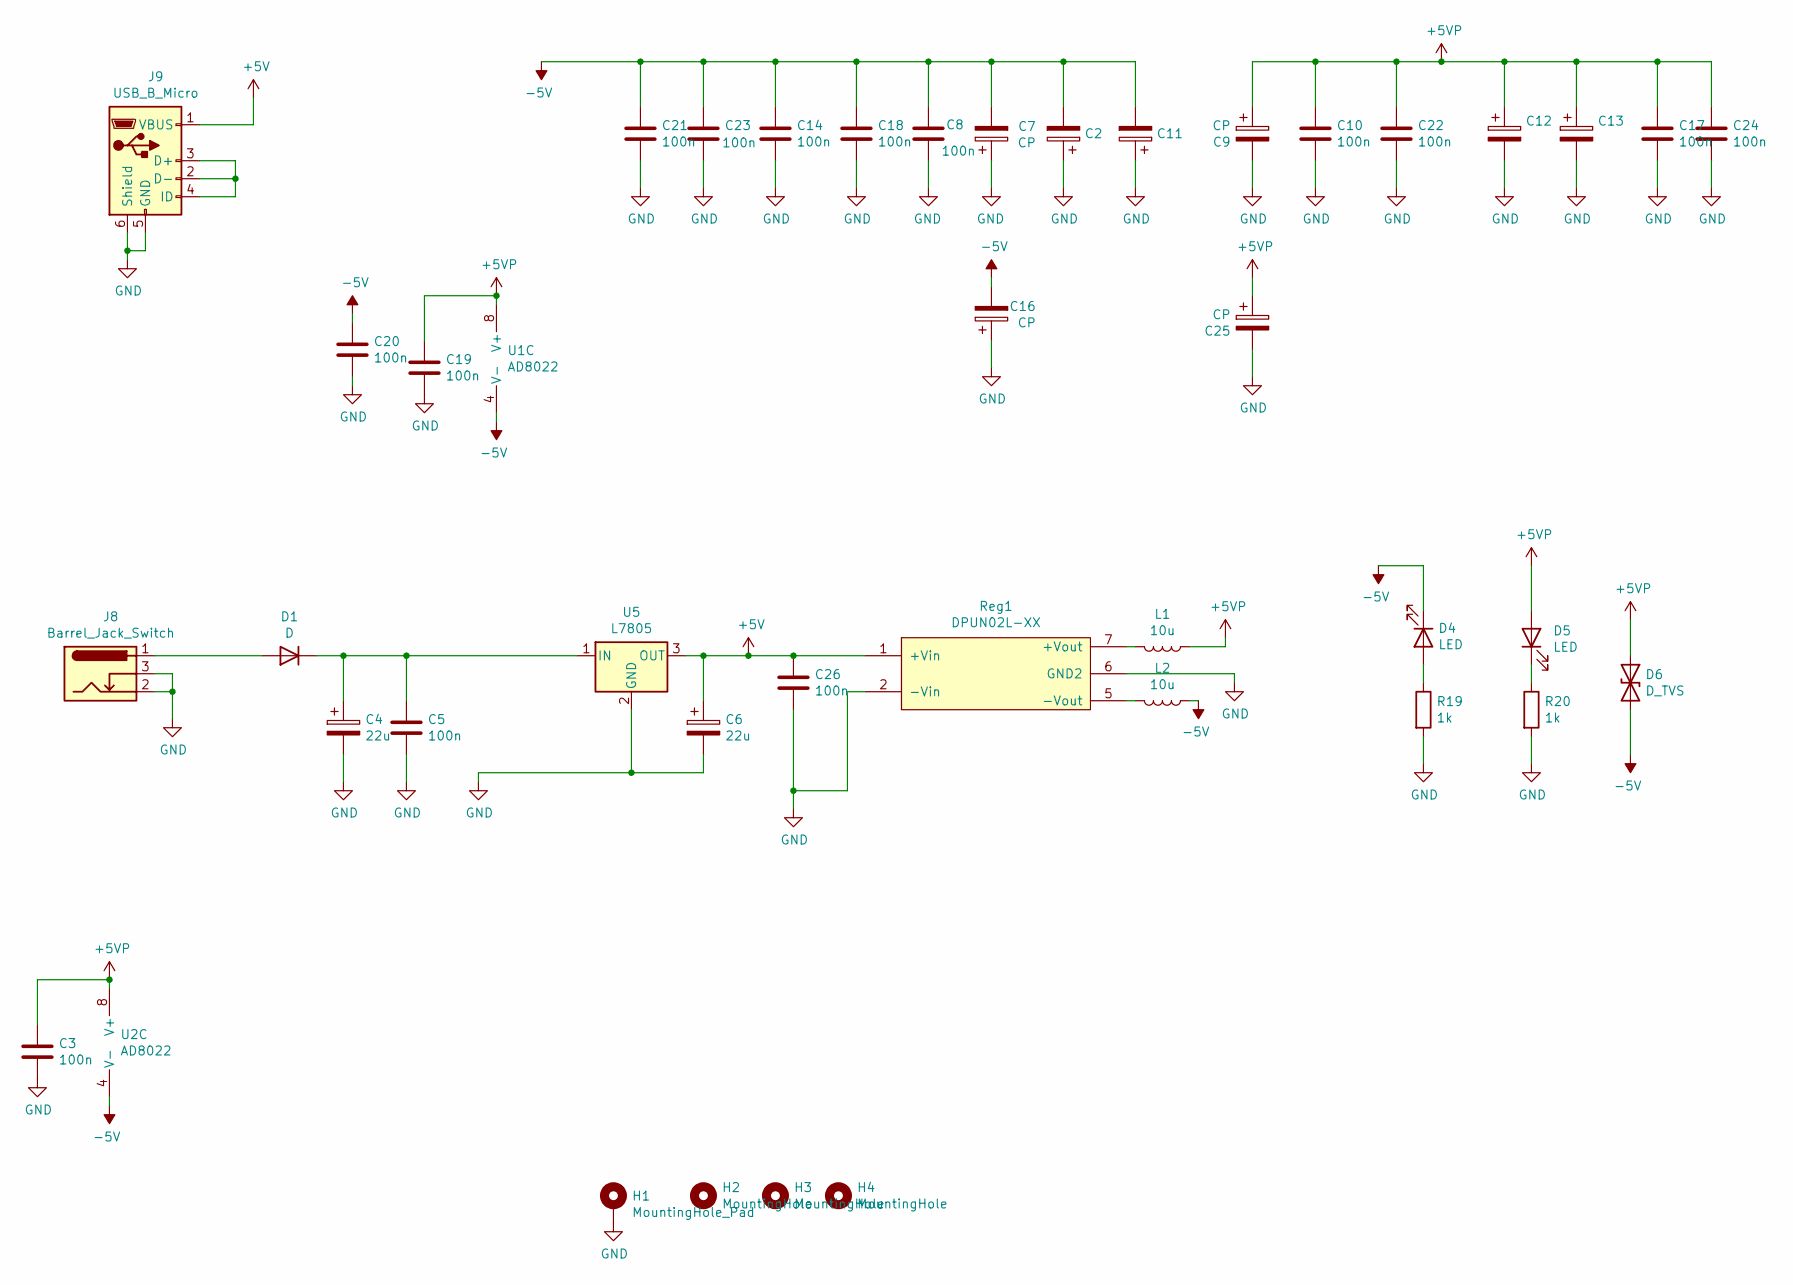
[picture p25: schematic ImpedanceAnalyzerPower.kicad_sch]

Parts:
C2, C11, C12, C13: C_Polarized; C_1206_3216Metric_Pad1.33x1.80mm_HandSolder
C3, C5, C8, C10, C14, C17, C18, C19, C20, C21, C22, C23, C24, C26: 100n; C_0805_2012Metric
C4, C6: 22u; CP_Radial_D5.0mm_P2.00mm
C7, C9, C16, C25: CP; CP_Radial_D8.0mm_P5.00mm
D1: D; D_SMA
D4, D5: LED; LED_1206_3216Metric
D6: D_TVS; D_SMA
H1: MountingHole_Pad; MountingHole_4.3mm_M4_Pad
H2, H3, H4: MountingHole; MountingHole_4mm
J8: Barrel_Jack_Switch; BarrelJack_Horizontal
J9: USB_B_Micro; USB_Micro-B_Wuerth_629105150521
L1, L2: 10u; L_Taiyo-Yuden_NR-60xx_HandSoldering
R19, R20: 1k; R_1206_3216Metric
Reg1: DPUN02L-XX; SIP-2W-7
U1, U2: AD8022; SO-8_3.9x4.9mm_P1.27mm
U5: L7805; TO-220-3_Vertical

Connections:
+5V: C6.1, C26.1, J9.1 (VBUS), Reg1.1 (+Vin), U5.3 (OUT)
+5VP: C3.1, C9.1, C10.1, C12.1, C13.1, C17.1, C19.1, C22.1, C24.1, C25.1, D5.2 (A), D6.1 (A1), L1.1, U1.8 (V+), U2.8 (V+); also elsewhere on the board
-5V: C2.2, C7.2, C8.1, C11.2, C14.1, C16.2, C18.1, C20.1, C21.1, C23.1, D4.1 (K), D6.2 (A2), L2.1, U1.4 (V-), U2.4 (V-); also elsewhere on the board
GND: C2.1, C3.2, C4.2, C5.2, C6.2, C7.1, C8.2, C9.2, C10.2, C11.1, C12.2, C13.2, C14.2, C16.1, C17.2, C18.2, C19.2, C20.2, C21.2, C22.2, C23.2, C24.2, C25.2, C26.2, H1.1, J8.2, J8.3, J9.5 (GND), J9.6 (Shield), R19.2, R20.2, Reg1.2 (-Vin), Reg1.6 (GND2), U5.2 (GND); also elsewhere on the board
unnamed: C4.1, C5.1, D1.1 (K), U5.1 (IN)
unnamed: D1.2 (A), J8.1
unnamed: D4.2 (A), R19.1
unnamed: D5.1 (K), R20.1
unnamed: J9.2 (D-), J9.3 (D+), J9.4 (ID)
unnamed: L1.2, Reg1.7 (+Vout)
unnamed: L2.2, Reg1.5 (-Vout)

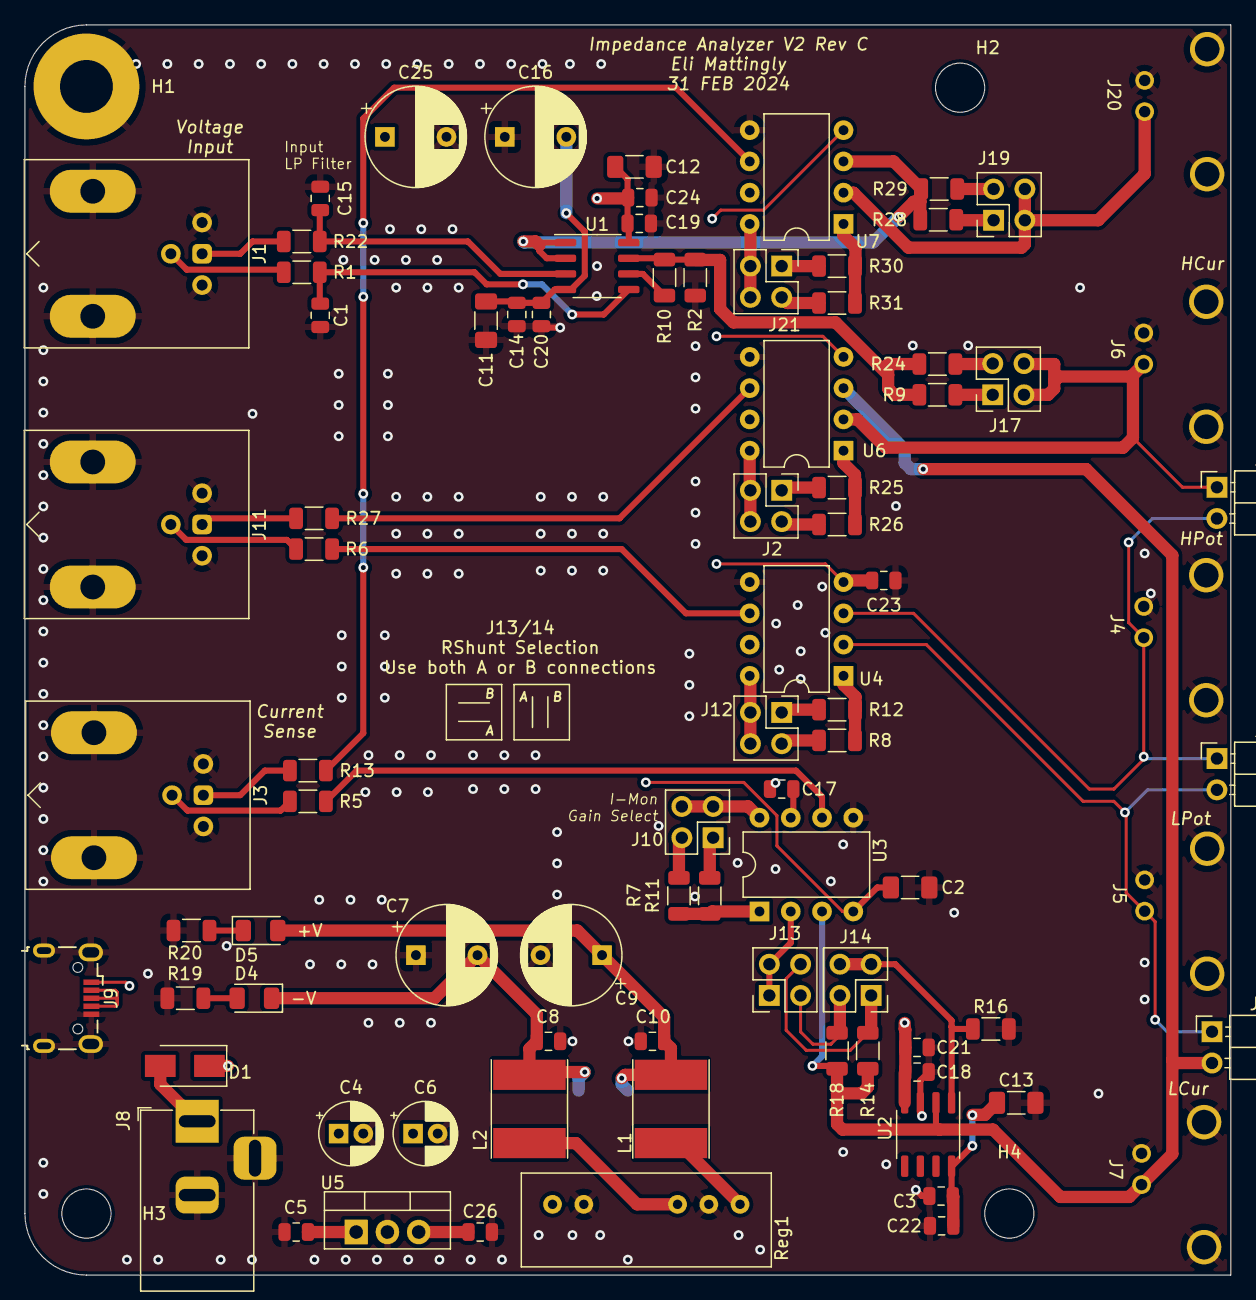
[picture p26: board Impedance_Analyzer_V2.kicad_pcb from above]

Board: 4 copper layers, 98.0 x 101.6 mm, 90 parts (1 on the bottom side), 55 nets.

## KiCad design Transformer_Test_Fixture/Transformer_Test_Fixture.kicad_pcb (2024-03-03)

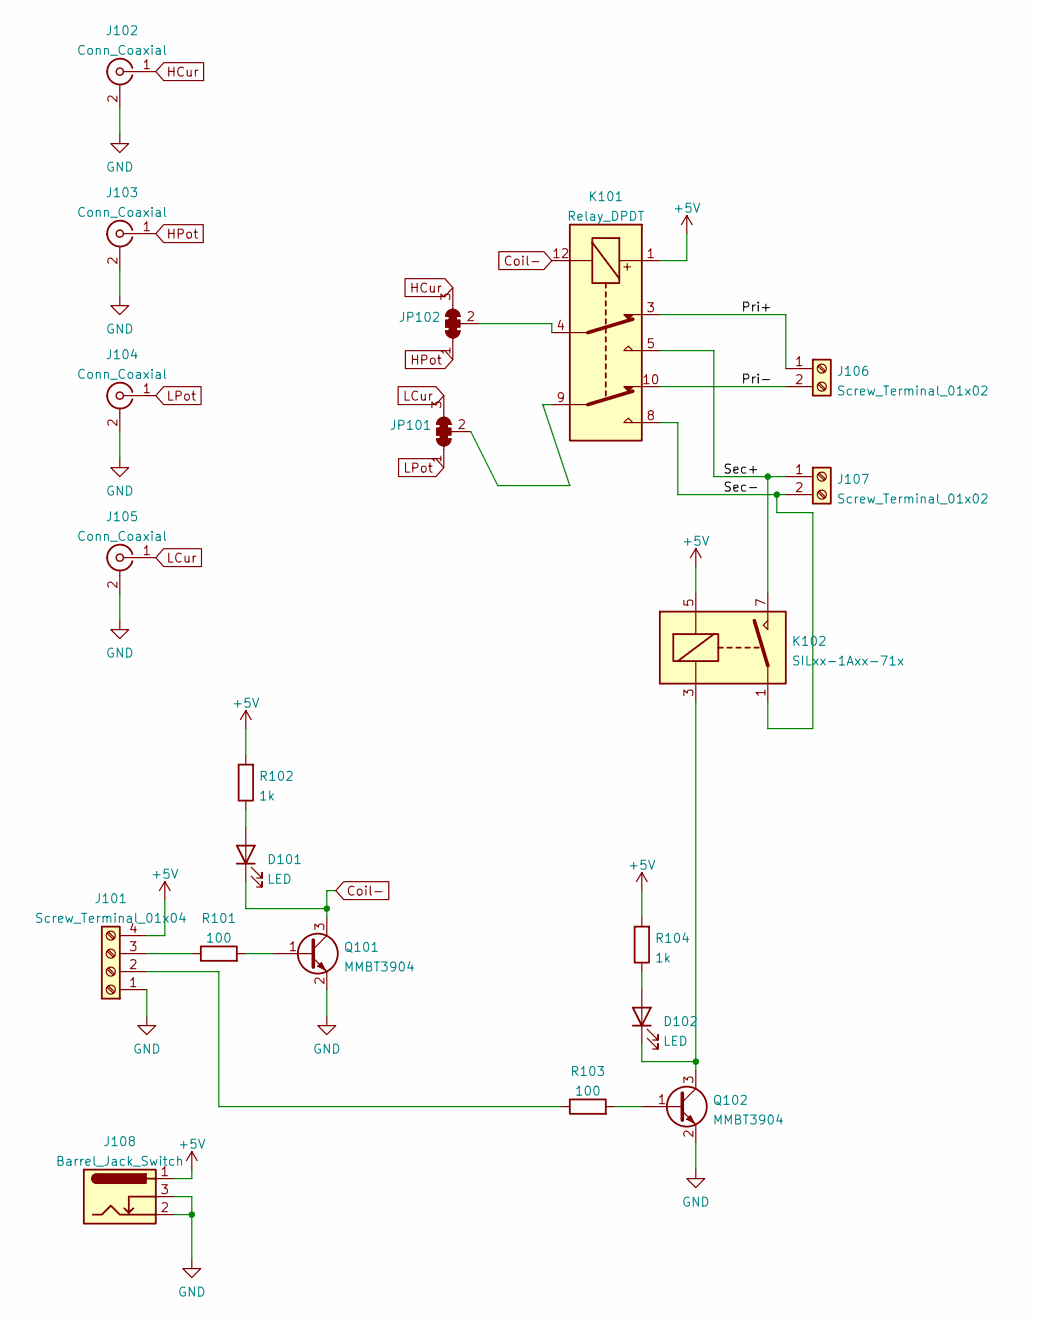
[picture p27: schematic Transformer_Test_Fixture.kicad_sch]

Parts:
D101, D102: LED; LED_0805_2012Metric_Pad1.15x1.40mm_HandSolder
J101: Screw_Terminal_01x04; TerminalBlock_bornier-4_P5.08mm
J102, J103, J104, J105: Conn_Coaxial; BNC_Amphenol_B6252HB-NPP3G-50_Horizontal
J106, J107: Screw_Terminal_01x02; TerminalBlock_bornier-2_P5.08mm
J108: Barrel_Jack_Switch; BarrelJack_GCT_DCJ200-10-A_Horizontal
JP101, JP102: SolderJumper_3_Bridged123; SolderJumper-3_P1.3mm_Bridged12_RoundedPad1.0x1.5mm
K101: Relay_DPDT; Relay_DPDT_Omron_G6S-2
K102: SILxx-1Axx-71x; Relay_SPST_StandexMeder_SIL_Form1A
Q101, Q102: MMBT3904; SOT-23
R101, R103: 100; R_0805_2012Metric
R102, R104: 1k; R_0805_2012Metric

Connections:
+5V: J101.4, J108.1, K101.1, K102.5, R102.2, R104.2
/Pri+: J106.1, K101.3
/Pri-: J106.2, K101.10
/Sec+: J107.1, K101.5, K102.7
/Sec-: J107.2, K101.8, K102.1
Coil-: D101.1 (K), K101.12, Q101.3 (C)
GND: J101.1, J102.2 (Ext), J103.2 (Ext), J104.2 (Ext), J105.2 (Ext), J108.2, J108.3, Q101.2 (E), Q102.2 (E)
HCur: J102.1 (In), JP102.3 (B)
HPot: J103.1 (In), JP102.1 (A)
LCur: J105.1 (In), JP101.3 (B)
LPot: J104.1 (In), JP101.1 (A)
unnamed: D101.2 (A), R102.1
unnamed: D102.1 (K), K102.3, Q102.3 (C)
unnamed: D102.2 (A), R104.1
unnamed: JP101.2 (C), K101.9
unnamed: JP102.2 (C), K101.4
unnamed: Q101.1 (B), R101.2
unnamed: Q102.1 (B), R103.2
unnamed: J101.3, R101.1
unnamed: J101.2, R103.1

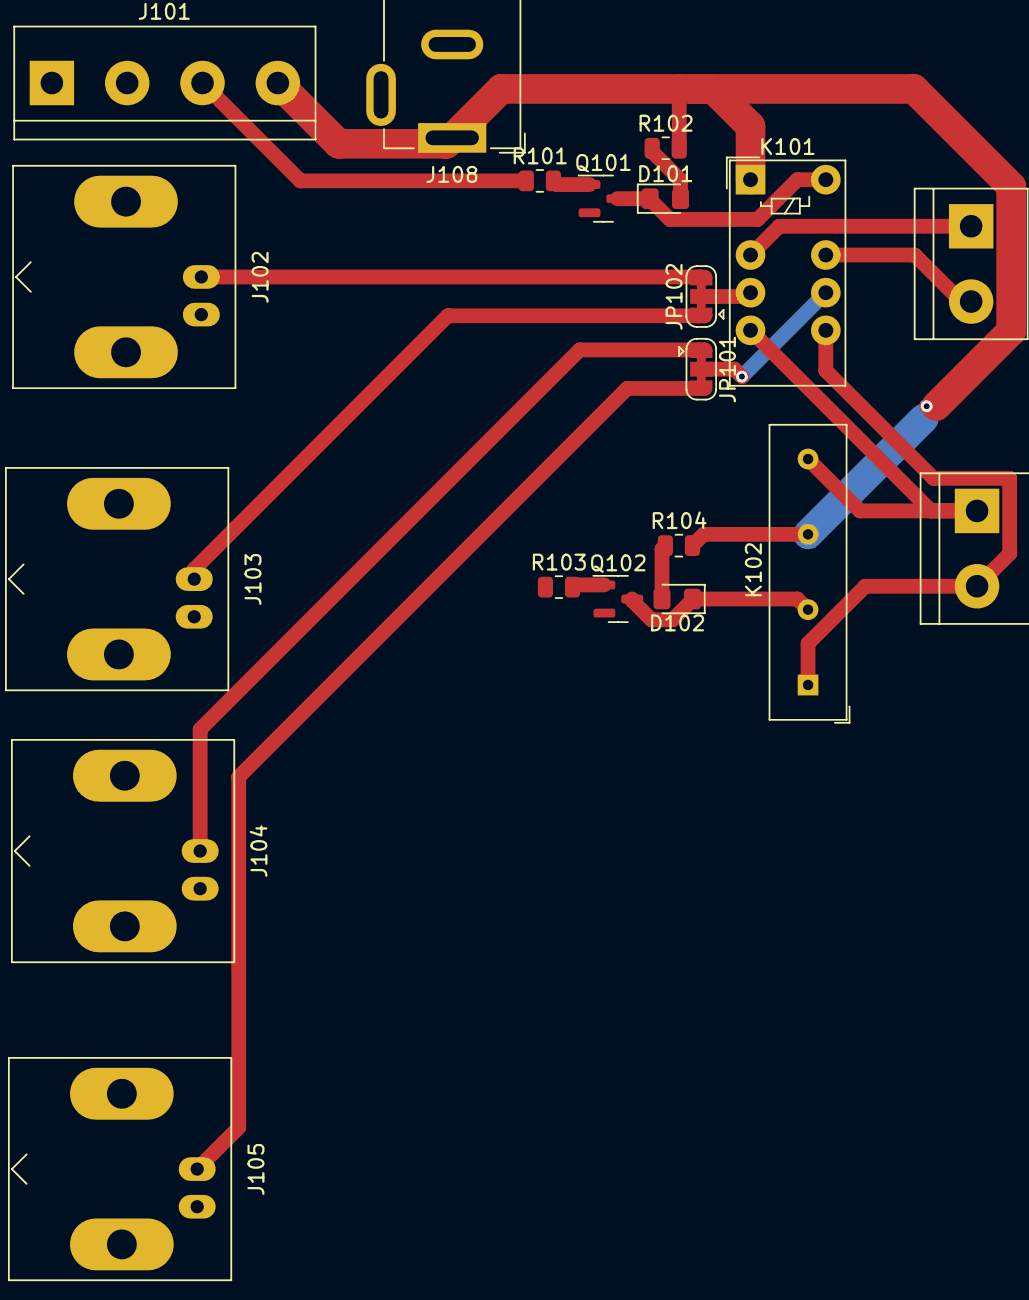
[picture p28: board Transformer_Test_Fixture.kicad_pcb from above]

Board: 2 copper layers, 20 parts (0 on the bottom side), 20 nets.

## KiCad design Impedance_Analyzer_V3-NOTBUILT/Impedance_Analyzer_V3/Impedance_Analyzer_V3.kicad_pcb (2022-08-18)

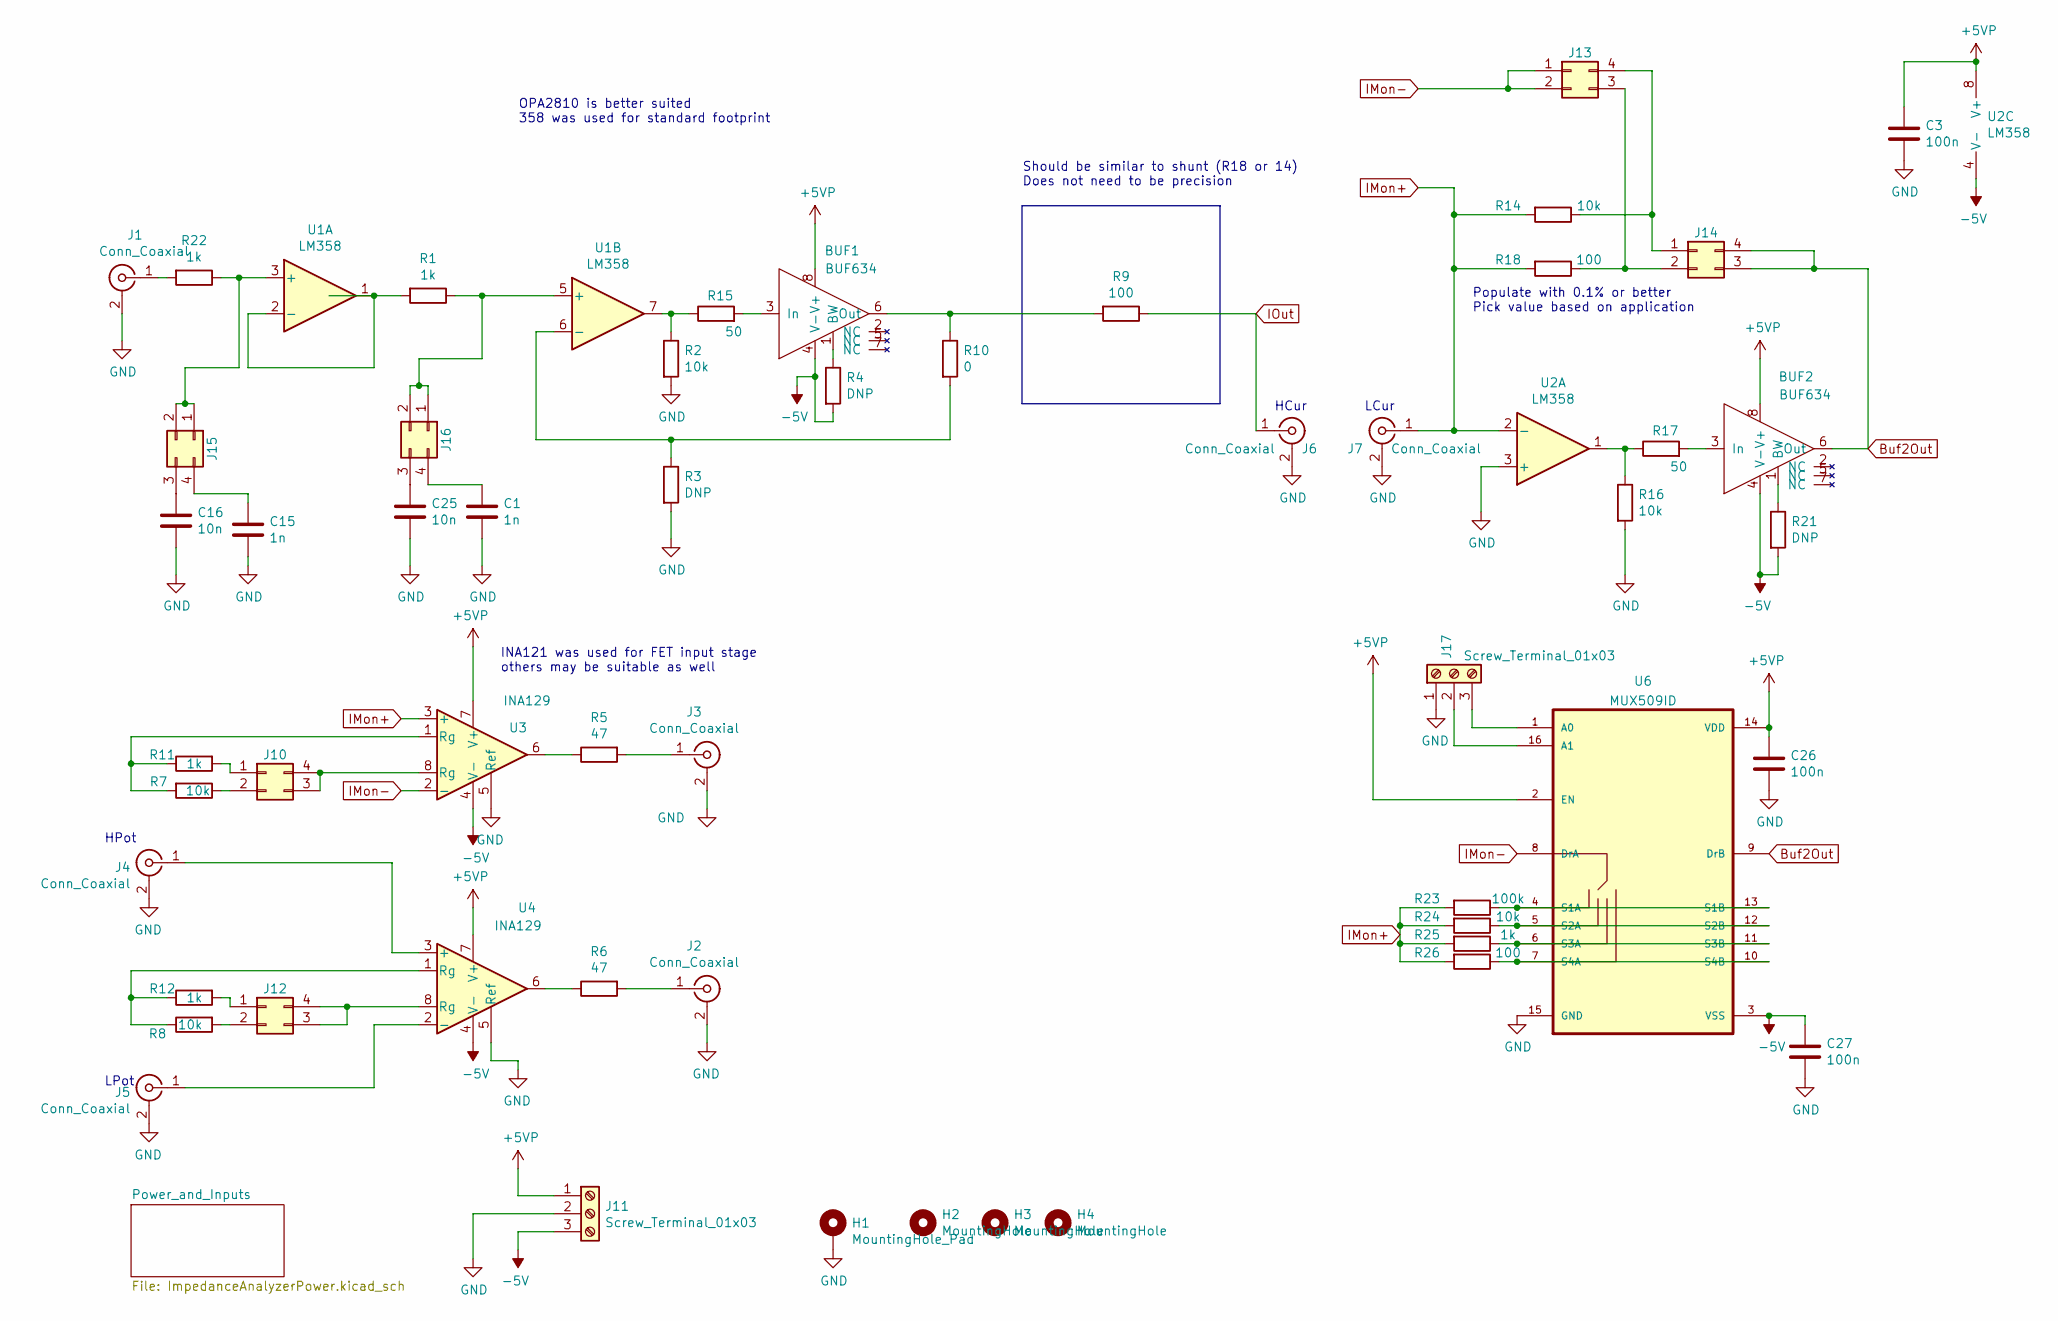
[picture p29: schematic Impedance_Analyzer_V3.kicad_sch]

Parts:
BUF1, BUF2: BUF634; SO-8_3.9x4.9mm_P1.27mm
C1, C15: 1n; C_0805_2012Metric
C3, C26, C27: 100n; C_0805_2012Metric
C16, C25: 10n; C_0805_2012Metric
H1: MountingHole_Pad; MountingHole_4.3mm_M4_Pad
H2, H3, H4: MountingHole; MountingHole_4mm
J1, J2, J3, J4, J5, J6, J7: Conn_Coaxial; BNC_TEConnectivity_1478204_Vertical
J10, J12, J13, J14, J15, J16: Conn_02x02_Counter_Clockwise; PinHeader_2x02_P2.54mm_Vertical
J11, J17: Screw_Terminal_01x03; TerminalBlock_bornier-3_P5.08mm
R1, R11, R12, R22, R25: 1k; R_1206_3216Metric
R2, R7, R8, R14, R16, R24: 10k; R_1206_3216Metric
R3, R4, R21: DNP; R_1206_3216Metric
R5, R6: 47; R_1206_3216Metric
R9, R18, R26: 100; R_1206_3216Metric
R10: 0; R_1206_3216Metric
R15, R17: 50; R_1206_3216Metric
R23: 100k; R_1206_3216Metric
U1, U2: LM358; SO-8_3.9x4.9mm_P1.27mm
U3, U4: INA129; DIP-8_W7.62mm
U6: MUX509ID; SOIC-16_3.9x9.9mm_P1.27mm

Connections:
+5VP: BUF1.8 (V+), BUF2.8 (V+), C3.1, C26.1, J11.1, U2.8 (V+), U3.7 (V+), U4.7 (V+), U6.2 (EN), U6.14 (VDD); also elsewhere on the board
-5V: BUF1.4 (V-), BUF2.4 (V-), C27.1, J11.3, R4.2, R21.2, U2.4 (V-), U3.4 (V-), U4.4 (V-), U6.3 (VSS); also elsewhere on the board
Buf2Out: BUF2.6 (Out), J14.3, J14.4, U6.9 (DrB)
GND: C1.2, C3.2, C15.2, C16.2, C25.2, C26.2, C27.2, H1.1, J1.2 (Ext), J2.2 (Ext), J3.2 (Ext), J4.2 (Ext), J5.2 (Ext), J6.2 (Ext), J7.2 (Ext), J11.2, J17.1, R2.2, R3.2, R16.2, U2.3 (+), U3.5 (Ref), U4.5 (Ref), U6.15 (GND); also elsewhere on the board
IMon+: J7.1 (In), R14.2, R18.2, R23.2, R24.2, R25.2, R26.2, U2.2 (-), U3.3 (+)
IMon-: J13.1, J13.2, U3.2 (-), U6.8 (DrA)
IOut: J6.1 (In), R9.1
unnamed: BUF1.1 (BW), R4.1
unnamed: BUF1.3 (In), R15.2
unnamed: BUF1.6 (Out), R9.2, R10.1
unnamed: BUF2.1 (BW), R21.1
unnamed: BUF2.3 (In), R17.2
unnamed: C1.1, J16.4
unnamed: C15.1, J15.4
unnamed: C16.1, J15.3
unnamed: C25.1, J16.3
unnamed: J1.1 (In), R22.2
unnamed: J2.1 (In), R6.2
unnamed: J3.1 (In), R5.2
unnamed: J4.1 (In), U4.3 (+)
unnamed: J5.1 (In), U4.2 (-)
unnamed: J10.1, R11.2
unnamed: J10.2, R7.1
unnamed: J10.3, J10.4, U3.8 (Rg)
unnamed: J12.1, R12.2
unnamed: J12.2, R8.2
unnamed: J12.3, J12.4, U4.8 (Rg)
unnamed: J13.3, J14.2, R18.1
unnamed: J13.4, J14.1, R14.1
unnamed: J15.1, J15.2, R22.1, U1.3 (+)
unnamed: J16.1, J16.2, R1.1, U1.5 (+)
unnamed: J17.2, U6.16 (A1)
unnamed: J17.3, U6.1 (A0)
unnamed: R1.2, U1.1, U1.2 (-)
unnamed: R5.1, U3.6
unnamed: R6.1, U4.6
unnamed: R3.1, R10.2, U1.6 (-)
unnamed: R7.2, R11.1, U3.1 (Rg)
unnamed: R8.1, R12.1, U4.1 (Rg)
unnamed: R2.1, R15.1, U1.7
unnamed: R16.1, R17.1, U2.1
unnamed: R23.1, U6.4 (S1A), U6.13 (S1B)
unnamed: R24.1, U6.5 (S2A), U6.12 (S2B)
unnamed: R25.1, U6.6 (S3A), U6.11 (S3B)
unnamed: R26.1, U6.7 (S4A), U6.10 (S4B)

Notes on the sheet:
HCur
Should be similar to shunt (R18 or 14) Does not need to be precision
INA121 was used for FET input stage others may be suitable as well
LCur
LPot
HPot
OPA2810 is better suited 358 was used for standard footprint
Populate with 0.1% or better Pick value based on application

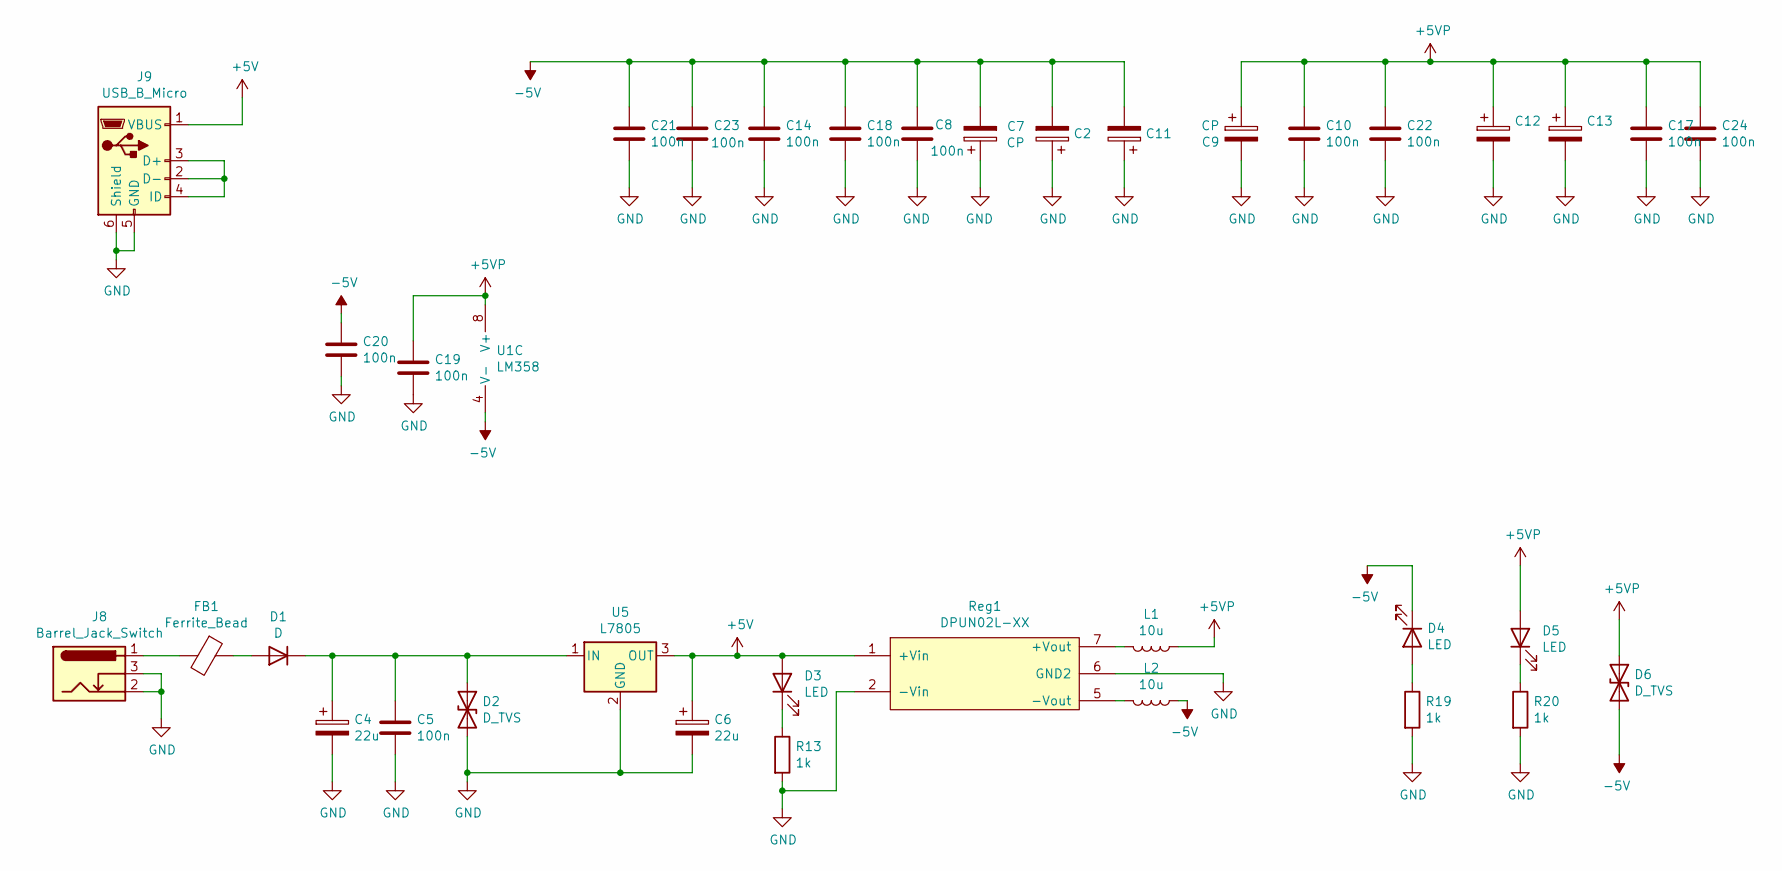
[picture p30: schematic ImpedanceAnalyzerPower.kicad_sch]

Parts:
C2, C11, C12, C13: C_Polarized; CP_EIA-6032-20_AVX-F_Pad2.25x2.35mm_HandSolder
C4, C6: 22u; CP_Radial_D5.0mm_P2.50mm
C5, C8, C10, C14, C17, C18, C19, C20, C21, C22, C23, C24: 100n; C_0805_2012Metric
C7, C9: CP; CP_Radial_D8.0mm_P5.00mm
D1: D; D_SMA
D2, D6: D_TVS; D_SMA
D3, D4, D5: LED; LED_1206_3216Metric
FB1: Ferrite_Bead; R_0805_2012Metric
J8: Barrel_Jack_Switch; BarrelJack_Horizontal
J9: USB_B_Micro; USB_Micro-B_Wuerth_629105150521
L1, L2: 10u; L_Taiyo-Yuden_NR-60xx_HandSoldering
R13, R19, R20: 1k; R_1206_3216Metric
Reg1: DPUN02L-XX; SIP-2W-7
U1: LM358; SO-8_3.9x4.9mm_P1.27mm
U5: L7805; TO-220-3_Vertical

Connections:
+5V: C6.1, D3.2 (A), J9.1 (VBUS), Reg1.1 (+Vin), U5.3 (OUT)
+5VP: C9.1, C10.1, C12.1, C13.1, C17.1, C19.1, C22.1, C24.1, D5.2 (A), D6.1 (A1), L1.1, U1.8 (V+); also elsewhere on the board
-5V: C2.2, C7.2, C8.1, C11.2, C14.1, C18.1, C20.1, C21.1, C23.1, D4.1 (K), D6.2 (A2), L2.1, U1.4 (V-); also elsewhere on the board
GND: C2.1, C4.2, C5.2, C6.2, C7.1, C8.2, C9.2, C10.2, C11.1, C12.2, C13.2, C14.2, C17.2, C18.2, C19.2, C20.2, C21.2, C22.2, C23.2, C24.2, D2.2 (A2), J8.2, J8.3, J9.5 (GND), J9.6 (Shield), R13.2, R19.2, R20.2, Reg1.2 (-Vin), Reg1.6 (GND2), U5.2 (GND); also elsewhere on the board
unnamed: C4.1, C5.1, D1.1 (K), D2.1 (A1), U5.1 (IN)
unnamed: D1.2 (A), FB1.1
unnamed: D3.1 (K), R13.1
unnamed: D4.2 (A), R19.1
unnamed: D5.1 (K), R20.1
unnamed: FB1.2, J8.1
unnamed: J9.2 (D-), J9.3 (D+), J9.4 (ID)
unnamed: L1.2, Reg1.7 (+Vout)
unnamed: L2.2, Reg1.5 (-Vout)

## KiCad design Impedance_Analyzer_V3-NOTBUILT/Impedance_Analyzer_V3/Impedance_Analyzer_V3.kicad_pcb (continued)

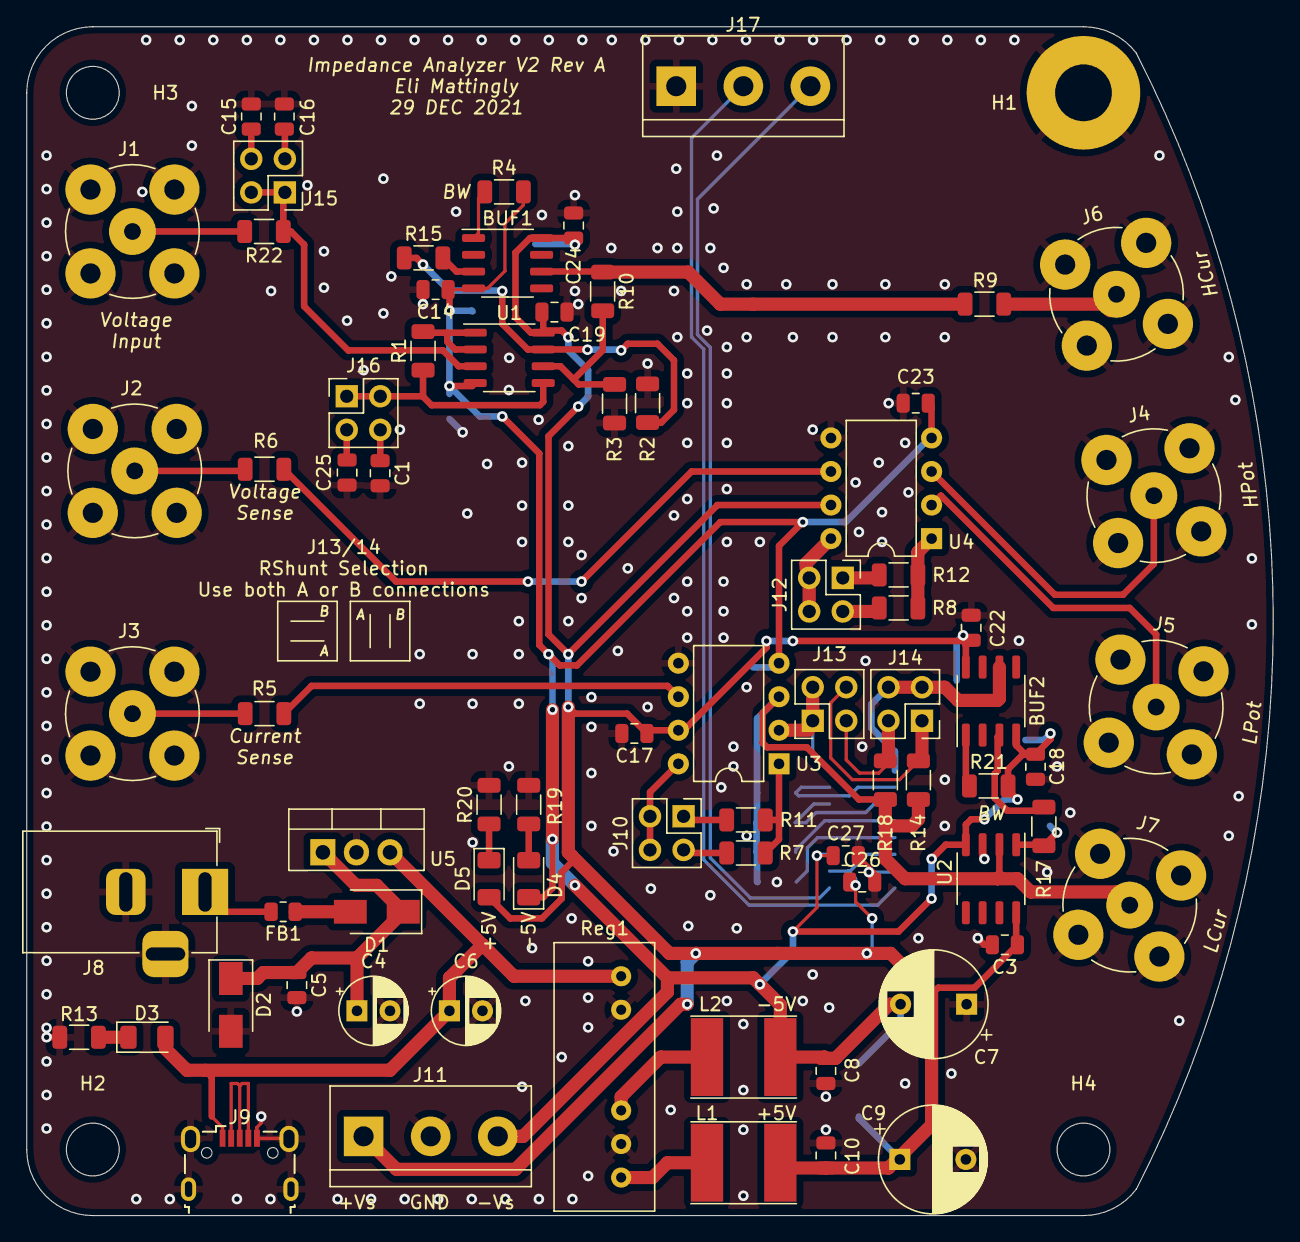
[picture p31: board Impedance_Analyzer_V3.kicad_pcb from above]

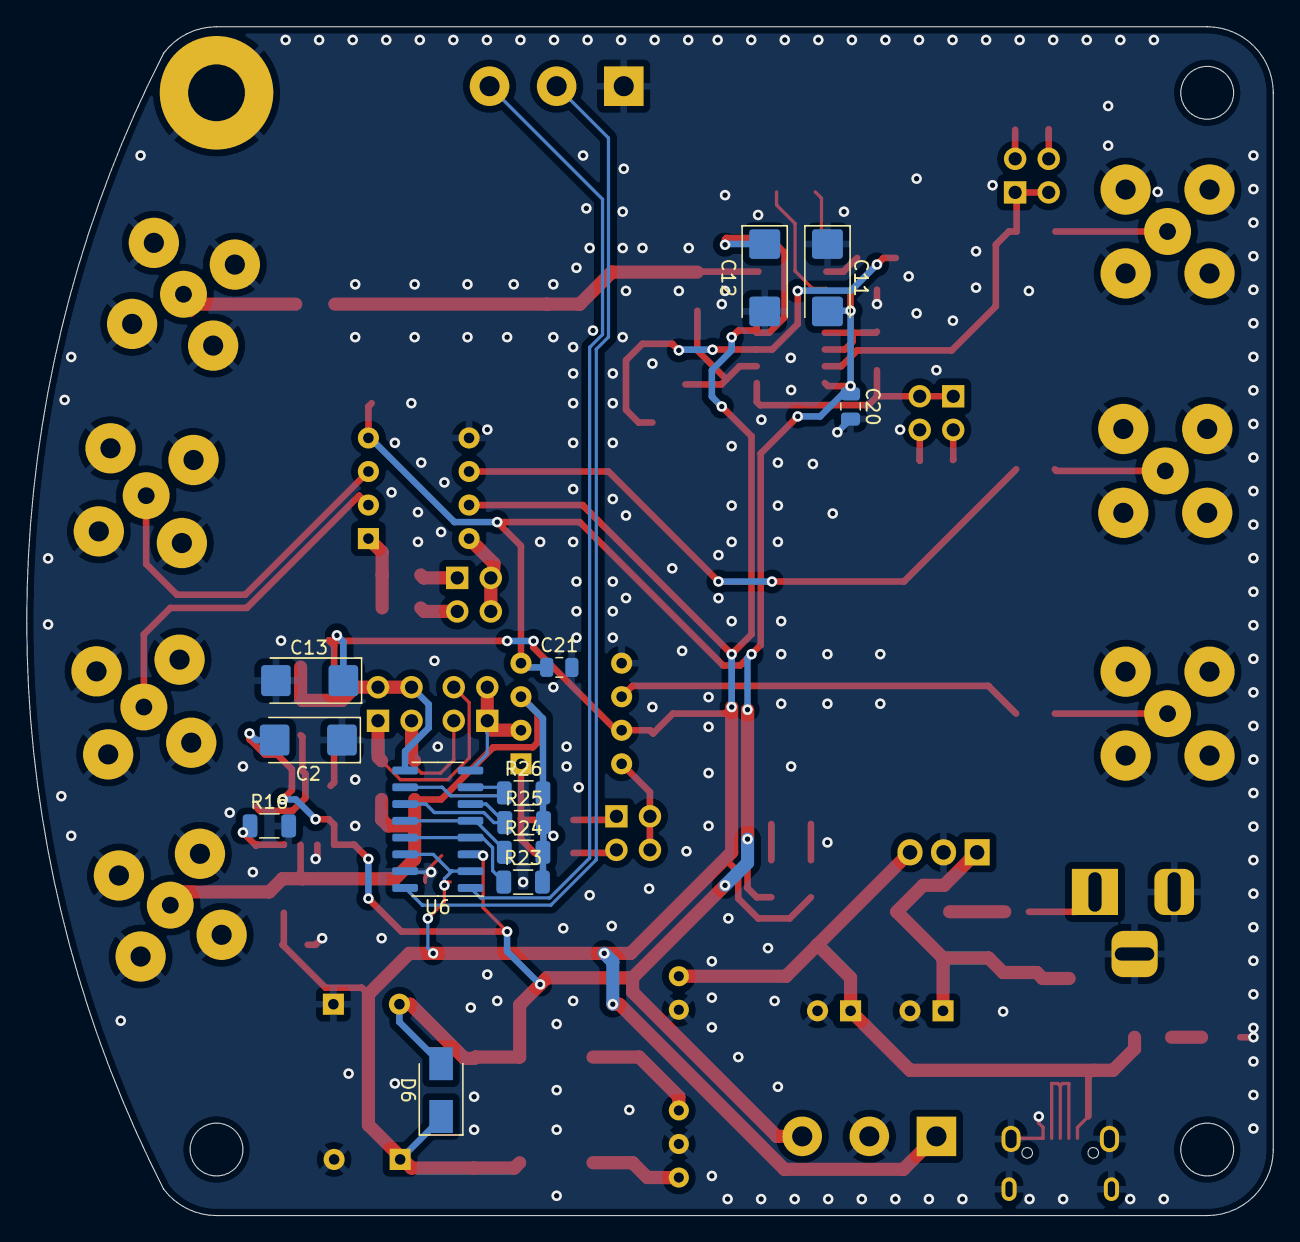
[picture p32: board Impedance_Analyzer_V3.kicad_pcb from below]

Board: 2 copper layers, 94.4 x 90.0 mm, 92 parts (13 on the bottom side), 55 nets.

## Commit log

2021-12-26 Formatting, Minor fixes
    [ImpedanceAnalyzerPower.kicad_sch, Impedance_Analyzer.kicad_pcb, Impedance_Analyzer.kicad_sch]
2021-12-30 Update LTSPICE, Minor board changes
    [AccuracyTesting.xlsx, ImpedanceAnalyzerPower.kicad_sch, Impedance_Analyzer.kicad_pcb, Impedance_Analyzer.kicad_sch]
2022-08-01 V2Rev B update schematic and add V3 folder
    [ImpedanceAnalyzerPower.kicad_sch, Impedance_Analyzer_V3-B_Cu.gbr, Impedance_Analyzer_V3-B_Mask.gbr, Impedance_Analyzer_V3-B_Paste.gbr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]
2022-08-14 Add BOM, update readme
    [Impedance_Analyzer_V2.csv, Impedance_Analyzer_V2_MouserBOM.xlsx]
2022-08-24 Add STEP file, minor changes
    [Impedance_Analyzer_V2-B_Cu.gbr, Impedance_Analyzer_V2-B_Mask.gbr, Impedance_Analyzer_V2-B_Paste.gbr, Impedance_Analyzer_V2-B_Silkscreen.gbr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]
2022-08-24 Add case
    [Bottom Case.0001.ipt, Bottom Case.ipt, Bottom Case.stl, Impedance_Analyzer_V2 PCB.ipt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]
2022-09-02 Add Resistor Accuracy Testing
2022-09-04 Process data, make figs
    [Impedance_Analyzer_V2_MouserBOM.xlsx]
2022-09-05 Meas capacitors
2022-09-05 Update readme, comment in schematic
    [ImpedanceAnalyzerPower.kicad_sch, Impedance_Analyzer_V2.kicad_sch, Impedance_Analyzer_V3-B_Cu.gbr, Impedance_Analyzer_V3-B_Mask.gbr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]
2024-03-03 Make Rev C + Curve tracer init
    [CurveTracer.kicad_sch, ImpedanceAnalyzerPower.kicad_sch, Impedance_Analyzer_V2.kicad_pcb, Impedance_Analyzer_V2.kicad_sch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]
2024-04-28 Update Impedance board
    [CurveTracer.kicad_sch, Impedance_Analyzer_V2.kicad_pcb, Impedance_Analyzer_V2.kicad_sch]
